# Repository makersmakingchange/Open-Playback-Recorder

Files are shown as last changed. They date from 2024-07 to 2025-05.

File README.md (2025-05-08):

# Open Playback Recorder

The Open Playback Recorder can record three lists of voice messages that its user can playback via the trigger of an accessible button connected through a 3.5 mm mono jack. It aims to assist users with communication difficulties by giving them alternative methods to engage in conversation. This device has functionality similar to AbleNet’s Big Mack or Step by Step.  

The device is comprised of off-the-shelf electronics and 3D printed parts. The overall cost of materials is about $90 (plus $8 for component shipping).

The Open Playback Recorder is Open Assistive Technology (OpenAT) and is certified as Open Source Hardware by the Open Source Hardware Association under the OSHWA UID [CA000050](https://certification.oshwa.org/ca000050.html). Under the terms of the open source licenses, the device may be built, used, and improved upon by anyone.

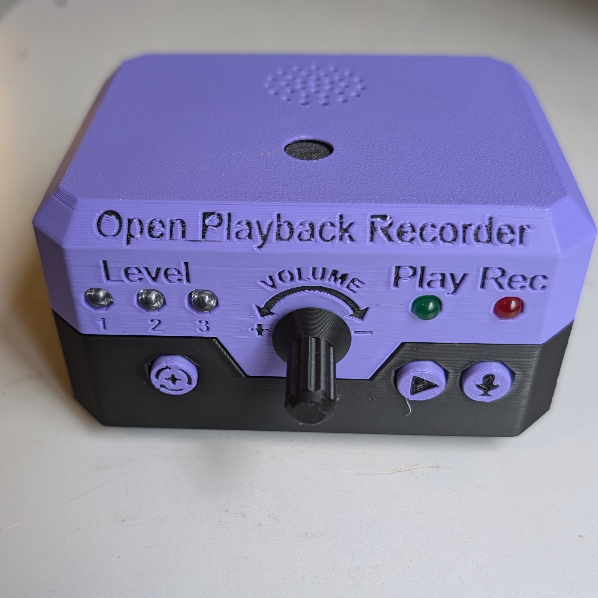
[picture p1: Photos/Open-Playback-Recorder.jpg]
An Open Playback Recorder with two Interact Switches with custom toppers.


## Makers Making Change Assistive Device Library
 - https://www.makersmakingchange.com/s/product/open-playback-recorder/01tJR000003DNOVYA4

## How to Obtain the Device
### 1. Do-it-Yourself (DIY) or Do-it-Together (DIT)

This is an open-source assistive technology, so anyone is free to build it. All of the files and instructions required to build the device are contained within this repository. Refer to the Maker Guide below.

### 2. Request a build of this device

You may also submit a build request through the [MMC Library Page](https://www.makersmakingchange.com/s/product/open-playback-recorder/01tJR000003DNOVYA4) to have a volunteer maker build the device. As the requestor, you are responsible for reimbursing the maker for the cost of materials and any shipping.

### 3. Build this device for someone else

If you have the skills and equipment to build this device, and would like to donate your time to create the device for someone who needs it, visit the [MMC Maker Wanted](https://makersmakingchange.com/maker-wanted/) section.

## Build Instructions

### 1. Read through the Maker Guide
The [Maker Guide](/Documentation/Open_Playback_Recorder_Maker_Guide.pdf)  contains all the necessary information to build this device, including tool lists, assembly instructions, programming instructions (if applicable) and testing.

### 2. Order the Off-The-Shelf Components
The [Bill of Materials](/Documentation/Open_Playback_Recorder_BOM.xlsx) lists all of the parts and components required to build the Open Playback Recorder. Several  components for this device will need to be ordered online.

### 3. Order the PCBs
The [PCB files](/Build_Files/PCB_Files) contain the Gerber files needed to order the PCBs, and instructions for how to order PCBs can be found in the [Maker Guide](/Documentation/Open_Playback_Recorder_Maker_Guide.pdf)

### 4. Print the 3D Printable components
All of the files and individual print files can be in the [/Build_Files/3D_Printing_Files](/Build_Files/3D_Printing_Files/) folder.

### 5. Assemble the Open Playback Recorder
Reference the [Maker Guide](/Documentation/Open_Playback_Recorder_Maker_Guide.pdf) for the tools and steps required to build each portion.

## How to improve this Device
As open source assistive technology, you are welcomed and encouraged to improve upon the design. 

## Files
### Documentation
| Document             | Version | Link |
|----------------------|---------|------|
| Design Rationale     | 2.0     | [Open_Playback_Recorder_Design_Rationale](/Documentation/Open_Playback_Recorder_Design_Rationale.pdf)     |
| Maker Guide          | 2.0     | [Open_Playback_Recorder_Maker_Checklist](/Documentation/Open_Playback_Recorder_Maker_Guide.pdf)     |
| Bill of Materials    | 2.0     | [Open_Playback_Recorder_Bill_of_Materials](/Documentation/Open_Playback_Recorder_BOM.xlsx)     |
| User Guide           | 2.0     | [Open_Playback_Recorder_User_Guide](/Documentation/Open_Playback_Recorder_User_Guide.pdf)    |
| Changelog            | 2.0     | [Open_Playback_Recorder_Changelog](CHANGES.txt)     |

### Design Files
 - [CAD Files](/Design_Files/CAD_Design_Files)
 - [PCB Files](/Design_Files/PCB_Files)

### Build Files
 - [3D Printing Files](/Build_Files/3D_Printing_Files)
 - [PCB Files](/Build_Files/PCB_Files)

### Software Files
 - [Software Files](/Build_Files/Firmware_Files)

## Attribution
Designers:
 - Neil Squire Society / Makers Making Change

Contributors:
 - Brad Wellington
 - Erik Steinthorson
 - Jake McIvor
 - Derrick Andrews

## License
Copyright (c) 2024 Neil Squire / Makers Making Change.

This repository describes Open Hardware:
 - Everything needed or used to design, make, test, or prepare the Open Playback Recorder is licensed under the [CERN 2.0 Weakly Reciprocal license (CERN-OHL-W v2) or later](https://cern.ch/cern-ohl ) .
 - All software is under the [GNU General Public License v3.0 (GPL-3.0)](https://www.gnu.org/licenses/gpl.html).
 - Accompanying material such as instruction manuals, videos, and other copyrightable works that are useful but not necessary to design, make, test, or prepare the Open Playback Recorder are published under a [Creative Commons Attribution-ShareAlike 4.0 license (CC BY-SA 4.0)](https://creativecommons.org/licenses/by-sa/4.0/) .

You may redistribute and modify this documentation and make products using it under the terms of the [CERN-OHL-W v2](https://cern.ch/cern-ohl).
This documentation is distributed WITHOUT ANY EXPRESS OR IMPLIED WARRANTY, INCLUDING OF MERCHANTABILITY, SATISFACTORY QUALITY AND FITNESS FOR A PARTICULAR PURPOSE.
Please see the CERN-OHL-W v2 for applicable conditions.

Source Location: https://github.com/makersmakingchange/Open-Playback-Recorder

---

<!-- ABOUT MMC START -->
## About Makers Making Change
[Makers Making Change Logo](https://www.makersmakingchange.com/)

Makers Making Change is a program of [Neil Squire](https://www.neilsquire.ca/), a Canadian non-profit that uses technology, knowledge, and passion to empower people with disabilities.

Makers Making Change leverages the capacity of community based Makers, Disability Professionals and Volunteers to develop and deliver affordable Open Source Assistive Technologies.

 - Website: [www.MakersMakingChange.com](https://www.makersmakingchange.com/)
 - GitHub: [makersmakingchange](https://github.com/makersmakingchange)
 - Twitter: [@makermakechange](https://twitter.com/makermakechange)
 - Instagram: [@makersmakingchange](https://www.instagram.com/makersmakingchange)
 - Facebook: [makersmakechange](https://www.facebook.com/makersmakechange)
 - LinkedIn: [Neil Squire Society](https://www.linkedin.com/company/neil-squire-society/)
 - Thingiverse: [makersmakingchange](https://www.thingiverse.com/makersmakingchange/about)
 - Printables: [MakersMakingChange](https://www.printables.com/@MakersMakingChange)

### Contact Us
For technical questions, to get involved, or to share your experience we encourage you to [visit our website](https://www.makersmakingchange.com/) or [contact us](https://www.makersmakingchange.com/s/contact).
<!-- ABOUT MMC END -->

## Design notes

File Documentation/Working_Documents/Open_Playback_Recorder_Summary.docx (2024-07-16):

# Product Information

## Product Name

Open Playback Recorder

## Device Category

Adapted Toys

Aids for Daily Living (ADL)

Assistive Switches

Communication Aids (AAC)

Computer Access

Environmental Controls

Gaming

Keyguard

Kits

LipSyncs

Mounting

Recreation and Leisure

Seating and Positioning

Switch Interfaces

Writing Aids

## User Value Statement

The Open Playback Recorder is an open-source device that can record three lists of voice messages that its user can playback via the trigger of an accessible button connected through a 3.5 mm mono jack. It aims to assist users with communication difficulties by giving them alternative methods to engage in conversation. This device has functionality similar to AbleNet’s Big Mack or Step by Step.

## Designer

Design by Neil Squire Society/Makers Making Change

# Device Info

## Overview

This device can record and store three separate lists of messages, which can then be sequentially played back using a 3.5mm jack or an onboard button. It is designed for users with difficulty communicating, and can allow them to choose from a list of messages for three separate situations.

## Disability Type

Select one or more disability types:

Agility / Dexterity

Arthritis

Cognitive

Hearing

Mobility

Mobility

Other

Pain

SCI

Vision

## Disability Type Description

This device is designed for users that have difficulty with communication and need a communication aid. This device can store three different sets of messages for use in three different situations.

## How To Use

### Setup

Connect two assistive switches, one to the jack labeled PLAY, and one to the jack labeled LEVEL.

### Power On

To power on the device, toggle the switch on the side of the device from OFF to ON.

### Message Recording

To record one or more messages, the device needs to be in Record Mode. The device will record messages to the currently selected level.

Step 1. To engage “Record Mode” hold down the REC button for 2 seconds. When Record Mode is engaged, the REC LED will turn red and remain solid.

Note: When Record Mode is engaged, all previous messages on that level will be erased.

Step 2. To start message recording, press and hold the PLAY button or assistive switch connected to the play jack. The REC LED will flash red. Record the message into the microphone and release the button to end and save the message. The RED LED will once again turn red and remain solid.

Step 3. To record additional messages, repeat Step 2.

Note: These messages will later by played back in the same order they were recorded.

Step 4. When the desired messages have been recorded, press the REC button to exit Record Mode. The red REC LED will turn off.

### Message Playback

To play back a message, press an assistive switch connected to the play jack. This will play a message from the current recording level. The play button on the device itself will also allow a secondary user to play a message. Continuing to press the button will cycle through all the messages on that level.

To change the message level, press an assistive switch connected to the level jack. The level shift button on the device will also allow a secondary user to change the message level. The current level will be indicated by the three blue LEDs on the left side of the device.

## Estimated Cost

The estimated material cost of the device:

$0 - $10

$11 - $25

$26 - $50

$51 - $100

$101 - $250

$250+

## Attribution

Design by Neil Squire Society/Makers Making Change

# Maker Info

## Project Skills

3D Printing

Custom PCB

Electronics

Laser Cutting

Mechanics

Other

Software

Soldering

Woodworking

## Skills Description

The primary skill used in this build is soldering. The circuit is constructed on a PCB, with all the components soldered to it.

## Tools Needed

3D Printer

Common Hand Tools

Common Power Tools

Laser Cutter

Soldering Iron

Specialized Tooling

## Print time (hrs)

3.5 hrs

## Assembly time (hrs)

0.5 hrs

## Build Instructions

The main work on this build involves soldering together two circuits on PCBs, one for each half of the enclosure.

## Download Link

## https://github.com/makersmakingchange/Open-Playback-Recorder/archive/refs/heads/main.zip

## Project Link

## https://github.com/makersmakingchange/Open-Playback-Recorder

# License

## License

- Everything needed or used to design, make, test, or prepare the Open Playback Recorder is licensed under the CERN 2.0 Weakly Reciprocal license (CERN-OHL-W v2) (https://cern.ch/cern-ohl) or later .

- All software is under the GNU General Public License v3.0 (GPL-3.0) (https://www.gnu.org/licenses/gpl.html).

- Accompanying material such as instruction manuals, videos, and other copyrightable works that are useful but not necessary to design, make, test, or prepare the Open Playback Recorder are published under a Creative Commons Attribution-ShareAlike 4.0 license (CC BY-SA 4.0) (https://creativecommons.org/licenses/by-sa/4.0/).

© 2024 by Neil Squire Society This work is licensed under the CC BY SA 4.0 License: http://creativecommons.org/licenses/by-sa/4.0 Page 1 of 2

V2.0 | June 2024 Open Playback Recorder Summary

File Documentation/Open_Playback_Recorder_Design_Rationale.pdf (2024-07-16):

V2.0 | June 2024

## Open Playback Recorder

## DESIGN RATIONALE

© 2022-2024 by Neil Squire / Makers Making Change This work is licensed under the CC BY SA 4.0 License: http://creativecommons.org/licenses/by-sa/4.0
Files available at https://github.com/makersmakingchange/Open-Playback-Recorder/ | Page 1 of 44

### Introduction

The Open Playback Recorder is an open-source device that can record three lists of voice messages that its user can playback via the trigger of an accessible button connected through a 3.5 mm mono jack. It aims to assist users with communication difficulties by giving them alternative methods to engage in conversation. This device has functionality similar to AbleNet’s Big Mack or Step by Step.

### Research

### Commercial Products

Big Mack
The Big Mack is an audio recording and playback device that costs between $150 and $200. It can record a message with a maximum length of two minutes via the trigger of a record button. The stored message can then be played back after the trigger of a large accessible button. It has adjustable volume and is battery powered by a 9V battery.

Message from AbleNet (ablenetinc.com) (https://www.ablenetinc.com/bigmack/)

Message storage procedure (From AbleNet):

1. Ensure you've properly installed a 9V Alkaline battery into your device
2. Turn the device on
3. Press and hold the Record Switch until the LED lights up solid Red, then release the switch
4. Press and hold down the main switch top of your device. You will see the LED flashes Red when recording.
5. Speak your message into the communication device, then release the switch top to complete the recording
6. When finished, press the Record Switch one time to exit record mode

Button size: ~12 cm diameter

Little Mack: Little Mack = ~6 cm

Big Step by Step
Costing between around $220, the Big Step by Step is a similar product to the Big Mack with two additional features. This device can record a sequential list of messages with a maximum total length of four minutes. Each message in the list is played one by one for each press of the playback button. The second feature included is a 3-level switch where each level stores a unique list of messages.

## DESIGN RATIONALE

Files available at https://github.com/makersmakingchange/Open-Playback-Recorder/ | Page 2 of 44

BIG Step-by-Step (ablenetinc.com) (https://www.ablenetinc.com/big-step-by-step/)

Message Recording Procedure (From AbleNet)

1. Add one alkaline 9-volt battery to device (battery not included).
2. Turn device on.
3. Select desired level.
4. Press and hold record button until recording indicator light turns on.
5. Press and hold colored switch top. Begin speaking into microphone after you hear beep.
6. When done recording message, release colored switch top.
7. Repeat steps 5 and 6 to record additional messages.
8. Press the record button to turn the recording indicator light off.
9. Optional: Select a different recording level to record a second and third set of messages.
10. Adjust volume as needed.
11. Your device is ready to use.

Little Mack Options
Both styles of the Big Mack are also offered in smaller sizes for a similar cost.

https://www.spectronics.com.au/product/littlemack-communicator-enhanced

https://www.spectronics.com.au/product/little-step-by-step-communicator-with-levels-enhanced

Pet Training Button
There are a series of audio playback buttons designed for the use of trained pets. They are inexpensive, costing between $10 to $40 with the drawback of back functionality. They can record and store a single message with a maximum length of 10 to 30 seconds. Stored messages are played back via the trigger of a small button and has no volume control.

Neutral Record Talking Button : Amazon.ca: Office Products (https://www.amazon.ca/Neutral-Record-Talking-Button/dp/B073S3BKN6)

### DIY Projects

Project | Demonstrates | Link
Arduino Spy Bug | • Using Micro SD Modules with Arduino • Using microphone • Saving WAV files onto a micro-SD card | Make Your Own Spy Bug (Arduino Voice Recorder) : 5 Steps (with Pictures) -Instructables (https://www.instructables.com/Make-Your-Own-Spy-Bug-Arduino-Voice-Recorder/)
Arduino Spy Bug Remix | • Similar Project • Different micro controller | Simple Arduino Voice Recorder for Spy Bug Voice Recording (circuitdigest.com) (https://circuitdigest.com/microcontroller-projects/simple-arduino-voice-recorder-for-spy-bug-voice-recording)
Arduino Audio Player | • Audio Amp • Playing WAV files | Audio Player Using Arduino With Micro SD Card : 7 Steps (with Pictures) - Instructables (https://www.instructables.com/Audio-Player-Using-Arduino-With-Micro-SD-Card/)

## DESIGN RATIONALE

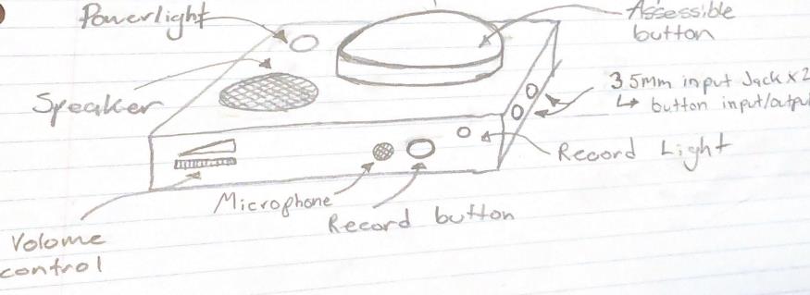
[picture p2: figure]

Files available at https://github.com/makersmakingchange/Open-Playback-Recorder/ | Page 3 of 44
Arduino Mp3 Player | • Similar project to Arduino Audio Player | Arduino Mp3 Player : 5 Steps -Instructables (https://www.instructables.com/Arduino-Mp3-Player/)
SD Card Experiments | • Using SD card modules with Arduino • Applications of SD cards | SD Card Experiments with Arduino | DroneBot Workshop (https://dronebotworkshop.com/sd-card-arduino/)

### Requirements

### Goals

G01 | Record and store a message with a minimum allowable record time of 4 minutes
G02 | Play stored message after trigger of an accessible button
G03 | Adjustable playback volume with maximum level loud enough to be heard within a room

### Functional Requirements

F01 | Total print time under 24 hours
F02 | Battery powered with easily obtainable batteries
F03 | Ability to be trigger by an external switch via a 3.5 mm mono cable

### Non-functional Requirement

NF01 | Exchangeable button cap designs for different needs of the user.
NF02 | Capable of interconnecting additional Open Playback Buttons
NF03 | Easy access to batteries for exchanging them.
NF04 | Must be easily cleaned

### Constraints

C01 Capable of being constructed using basic maker tools.

### Ideation

Idea #1: Basic concept with necessary components.

## DESIGN RATIONALE

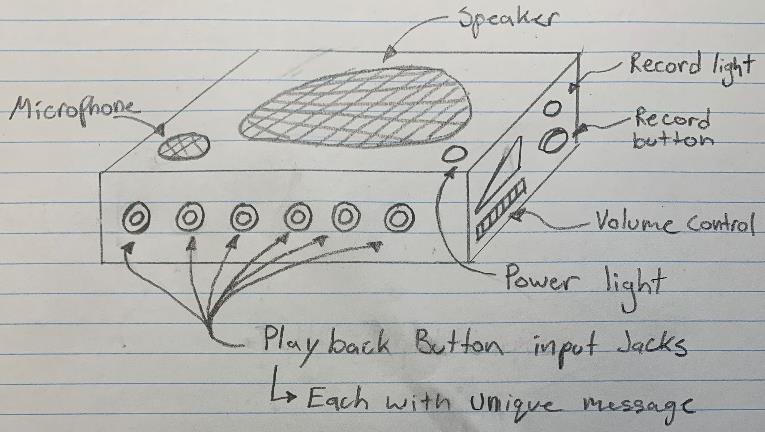
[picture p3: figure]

Files available at https://github.com/makersmakingchange/Open-Playback-Recorder/ | Page 4 of 44

Idea #2: Modular design utilizing external switches.

Instead of fitting all the electronics inside a large button, another idea could be to have a single unit to handle message recording and playback. An array of external buttons could then be plugged into one or many of the 3.5 mm input jacks. Each button would control its own message or sequential list of messages. This would allow for more space to fit larger speakers and electronics. The large assessable button would become its own device to be designed.

### Conceptual Design

### Options for Audio Recording and Playback

Option 1: Use of Voice Record and Playback Module
System | Possible Product | Notes: | Cost
Voice Record and Playback | SEN0197 DFRobot | Development Boards, Kits, Programmers | DigiKey (https://www.digikey.ca/en/products/detail/dfrobot/SEN0197/6588582) | SEN0197 • 10s Record time • Connects easily with Arduino | ~$10
| NC-ISD1620B Nuvoton Technology Corporation | Development Boards, Kits, Programmers | DigiKey (https://www.digikey.ca/en/products/detail/nuvoton-technology-corporation/NC-ISD1620B/1228829) | NC-ISD1620B • Single message • 6.6s to 40s record time | ~$10
| 107020007 Seeed Technology Co., Ltd | Development Boards, Kits, Programmers | DigiKey (https://www.digikey.ca/en/products/detail/seeed-technology-co-ltd/107020007/12177149) | Grove – Recorder V2.) • Volume control • 8Ω/2W Speaker • 8s to 20s record time | ~$10
Overall Notes | These modules are simple and easy to use while remaining inexpensive but may be to limiting functionally. As part of the requirements for this project, 4 minutes of record time is needed but these modules are intended for much shorter recordings. | | Total ~$30

## DESIGN RATIONALE

Files available at https://github.com/makersmakingchange/Open-Playback-Recorder/ | Page 5 of 44

Option 2: Use of Micro SD Storage
System | Component | Possible Product | Notes: | Cost
Controller | Arduino Micro | A000053 Arduino | Development Boards, Kits, Programmers | DigiKey (https://www.digikey.ca/en/products/detail/arduino/A000053/4486332) | Cheaper options? | ~$25
Audio Playback | Audio Amplifier Module | 2130 Adafruit | Mouser Canada (https://www.mouser.ca/ProductDetail/485-2130) | Pam8302A: • Mono sound • Shut off capabilities | ~$6
| Speaker | 3351 Adafruit | Mouser Canada (https://www.mouser.ca/ProductDetail/485-3351) | 3W 4 Ohm, 2.8” x 1.2” • Easy to mount • Recommended for Pam8302A or MAX98357A | ~$6
| Potentiometer: Volume Control | 3395 Adafruit | Mouser Canada (https://www.mouser.ca/ProductDetail/485-3395) | • 10K • Includes switch for on/off • Clicks in off position | ~$2
Audio Recording/ Storage | Micro Sd Reader: | 254 Adafruit | Mouser Canada (https://www.mouser.ca/ProductDetail/485-254) | Built in 3v-5v regulator | ~$10
| Micro Sd Card: Message Storage | COM-15107 SparkFun | Mouser Canada (https://www.mouser.ca/ProductDetail/474-COM-15107) | 1GB but many size options | ~$10
| Mic with Amp | 1713 Adafruit | Mouser Canada (https://www.mouser.ca/ProductDetail/485-1713) | | ~$10
Overall Notes | There is an added cost and complexity to using an SD card for storage. This solution requires an SD card module, SD card, audio recording module and must use a micro controller. However, this concept allows the full control of functionality. It will be possible to add modes for multiple message capabilities, i.e.: Big Mack mode, step by step mode, voice repeat mode, etc. Almost no limit on record time. | | | Total ~70

### Playing Audio Files

Recording and Playing Audio with Wav Files

For the Arduino use wav files for audio recording and playback, the TMRpcm library must be downloaded and used. This library is capable of reading wav files off an SD card and outputting the audio signal through a selected port on the Arduino. It must be noted that by default, the audio recording capabilities are disabled. To enable these features, the library configurations must be edited.

In the file pcmConfig.h file, there are two sections that must be edited:

In the General User Defines section, the “//#define buffSize 128” line of code must be uncommented by removing the “//” from in front.

In the Advanced User Defines section, at the bottom, lines “//#define ENABLE_RECORDING” and “//#define BLOCK_COUNT 10000UL” must also be uncommented.

## DESIGN RATIONALE

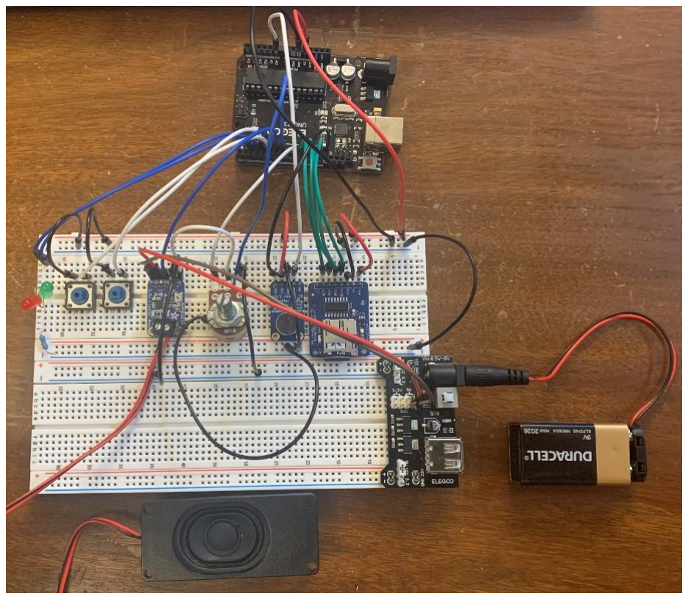
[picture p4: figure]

Files available at https://github.com/makersmakingchange/Open-Playback-Recorder/ | Page 6 of 44

### Using Audacity to Add Sound Indicators

Audacity is a program that can be used to create audio files. If these files are going to be played from the Arduino using the TMRpcm library, the files must be created and saved correctly.

Step 1.
At the bottom right corner, select Project Rate (Hz), and set to 3200, 22050, 16000, or 11025

Note: 16000 Hz is the default sample rate for the TMRpcm library.

Step 2.
At the top of the screen, click Tracks -> Add New -> and select Mono Track. Create one or more of the mono tracks to create the sound file
Step 3.
Once the sound is complete, click File -> Export -> Export Audio… -> save as type: Other uncompressed files, Header: WAV, Encoding: Signed 8-bit PCM

The audio file can now be saved and added to the device Micro SD card to be used by the TMRpcm library.

### V0.1 Proof-of-Concept Prototype

## DESIGN RATIONALE

Files available at https://github.com/makersmakingchange/Open-Playback-Recorder/ | Page 7 of 44

### POC Components

System | Component | Possible Product | Notes:
Controller | Micro Controller | Arduino Uno | Cheaper options?
Audio Playback | Audio Amplifier Module | 2130 Adafruit | Mouser Canada (https://www.mouser.ca/ProductDetail/485-2130) | Pam8302A: • Mono sound • Shut off capabilities
| Speaker | 3351 Adafruit | Mouser Canada (https://www.mouser.ca/ProductDetail/485-3351) | 3W 4 Ohm, 2.8” x 1.2” • Easy to mount. • Recommended for Pam8302A or MAX98357A
| Capacitor | | Protect speaker amplifier input voltage. • For use with PAM8302A 0.1uF to 0.22uF is ideal • low leakage tantalum or ceramic capacitor is the best choice
| Potentiometer: Volume Control | 3395 Adafruit | Mouser Canada (https://www.mouser.ca/ProductDetail/485-3395) | • 10K Ohm • Includes switch for on/off. • Clicks in off position
Audio Recording/ Storage | Micro SD Reader: | 254 Adafruit | Mouser Canada (https://www.mouser.ca/ProductDetail/485-254) | • Built in 3v-5v regulator. • Connects to SPI pins
| Micro SD Card: Message Storage | COM-15107 SparkFun | Mouser Canada (https://www.mouser.ca/ProductDetail/474-COM-15107) | 1GB but many size options
| Mic with Amp | 1713 Adafruit | Mouser Canada (https://www.mouser.ca/ProductDetail/485-1713)
Basic Control | Playback Button | B3F-5050 Omron Electronics | Mouser Canada (https://www.mouser.ca/ProductDetail/Omron-Electronics/B3F-5050?qs=dOLq8QE0Pqqk%2FO9x2OpTQw%3D%3D) | Simple press button
Record Button
Power/Play Light | LTL2R3KGD-EM Lite-On | Mouser Canada (https://www.mouser.ca/ProductDetail/Lite-On/LTL2R3KGD-EM?qs=xb8aMrBSZRJFqGZErUW7HQ%3D%3D) | Simple red and green LED’s
Record Light | LTL2R3KRD-EM Lite-On | Mouser Canada (https://www.mouser.ca/ProductDetail/Lite-On/LTL2R3KRD-EM?qs=xb8aMrBSZRL5MG5wqCOHaQ%3D%3D)

## DESIGN RATIONALE

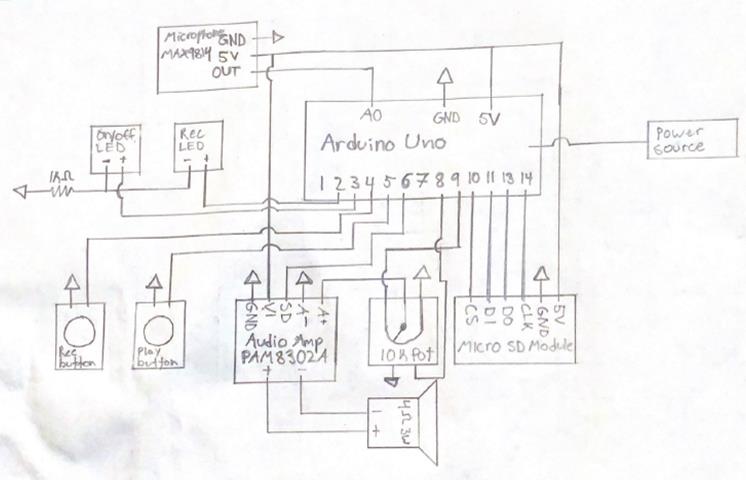
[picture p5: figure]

Files available at https://github.com/makersmakingchange/Open-Playback-Recorder/ | Page 8 of 44

### POC Wiring Diagram

### POC Device Functionality

Controls: | Playback Button: play button for primary user
| Record Button: small button for secondary user
| Volume Knob: small dial for secondary user
Indicators: | Power/Playback light: Green LED
| Record light: Red LED

Functionality: Power On/Off: small dial for secondary user.

| • Turn volume knob past minimum to power on device. • Power light turns on. • Turning the dial controls the volume output. • Clicking the dial into the minimum position turns the device off. • All lights turn off.
| Record Mode: Accessed via record button.
| • Hold Record Button for 2 seconds to engage record mode • Messages in storage are deleted. • Record light turns on.

## DESIGN RATIONALE

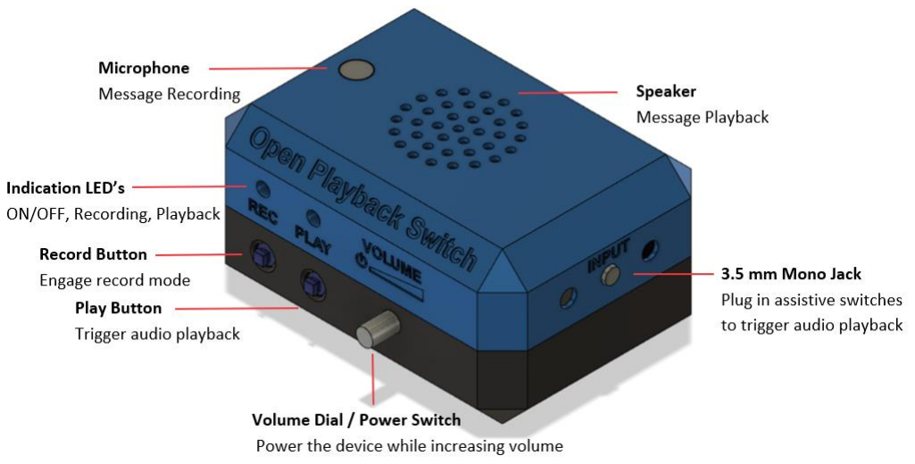
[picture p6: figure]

Files available at https://github.com/makersmakingchange/Open-Playback-Recorder/ | Page 9 of 44
- Press and hold Playback Button to record a message.
- Record light flashes during recording.

Message Playback: Accessed via play button.

- Press playback button to play message.
- Each trigger plays next message in queue.
- Goes back to first message after last message in queue is played.

### V0.2 MVP Design

### MVP Components

Component | Cost | Link
Micro Controller (Arduino Micro) | $30.50 | A000093 Arduino | Mouser Canada (https://www.mouser.ca/ProductDetail/782-A000093)
Audio Amplifier (Pam8302) | $5.45 | 2130 Adafruit | Mouser Canada (https://www.mouser.ca/ProductDetail/485-2130)
Mono Speaker (4Ω 3W ) | $5.45 | 3351 Adafruit | Mouser Canada (https://www.mouser.ca/ProductDetail/485-3351)
Potentiometer with Switch (Log) | $2.07 | 3481 Adafruit | Mouser Canada (https://www.mouser.ca/ProductDetail/485-3481)
Micro SD Reader | $10.35 | 254 Adafruit | Mouser Canada (https://www.mouser.ca/ProductDetail/485-254)
Micro SD Card | $9.49 | COM-15107 SparkFun | Mouser Canada (https://www.mouser.ca/ProductDetail/474-COM-15107)
Microphone (MAX9814) | $10.97 | 1713 Adafruit | Mouser Canada (https://www.mouser.ca/ProductDetail/485-1713)

## DESIGN RATIONALE

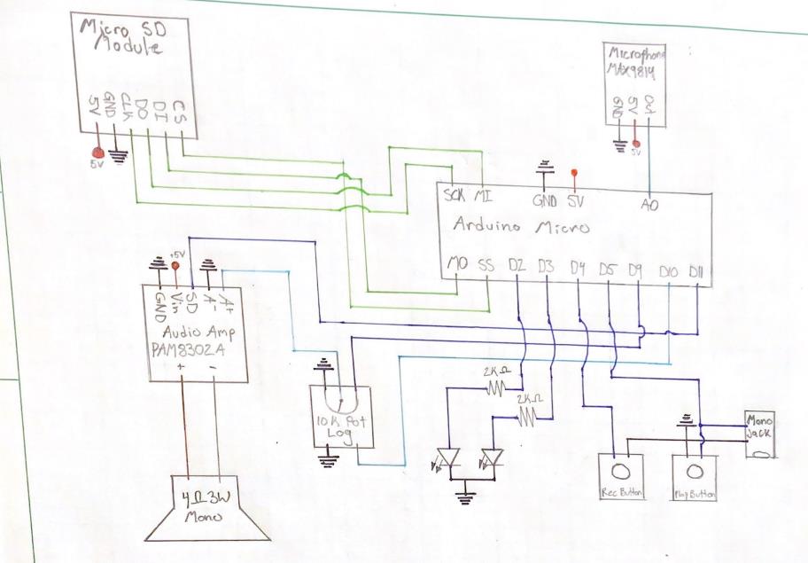
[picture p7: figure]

Files available at https://github.com/makersmakingchange/Open-Playback-Recorder/ | Page 10 of 44
Buttons (B3F-5050) | $1.52 | B3F-5050 Omron Electronics | Mouser Canada (https://www.mouser.ca/ProductDetail/Omron-Electronics/B3F-5050?qs=dOLq8QE0Pqqk%2FO9x2OpTQw%3D%3D)
3.5 mm Mono Jack | $1.95 | 35RAPC2AV Switchcraft | Mouser Canada (https://www.mouser.ca/ProductDetail/Switchcraft/35RAPC2AV?qs=I3kMT7EEIOWP5G1fR6CxcA%3D%3D)
Green LED (5 mm) | $0.44 | LTL2R3KGD-EM Lite-On | Mouser Canada (https://www.mouser.ca/ProductDetail/Lite-On/LTL2R3KGD-EM?qs=xb8aMrBSZRJFqGZErUW7HQ%3D%3D)
Red LED (5 mm) | $0.44 | LTL2R3KRD-EM Lite-On | Mouser Canada (https://www.mouser.ca/ProductDetail/Lite-On/LTL2R3KRD-EM?qs=xb8aMrBSZRL5MG5wqCOHaQ%3D%3D)
Resistor (1k Ω) | $0.66 | MBA02040C1001FRP00 Vishay / Beyschlag | Mouser Canada (https://www.mouser.ca/ProductDetail/Vishay-Beyschlag/MBA02040C1001FRP00?qs=LkqrmUh5PILp63ntvCnX0w%3D%3D)
Proto Half Breadboard | $6.21 | 1609 Adafruit | Mouser Canada (https://www.mouser.ca/ProductDetail/485-1609)
Male Through Hole Header | $0.80 | https://www.mouser.ca/ProductDetail/910-HDR100IMP40MGVTH (https://www.mouser.ca/ProductDetail/910-HDR100IMP40MGVTH)
Female Through Hole Header | $3.80 | HDR100IMP40F-G-V-TH Chip Quik | Mouser Canada (https://www.mouser.ca/ProductDetail/Chip-Quik/HDR100IMP40F-G-V-TH?qs=Wj%2FVkw3K%252BMB%252BpQKGESbrjQ%3D%3D)
Notes: | The MVP device uses many of the same electrical components as the POV. The key differences are: • A logarithmic potentiometer is used for increased volume control. • An Arduino Micro is used to decrease the size. • A mono jack is wired in parallel to the Play Button. • Electrical components are soldered to a protoboard. • Powered by a 9V battery in series with the power switch.

### MVP Wiring Diagram

### Feature Set

- Modular (i.e., standalone)

## DESIGN RATIONALE

Files available at https://github.com/makersmakingchange/Open-Playback-Recorder/ | Page 11 of 44

The MVP will be a modular device intended to be used with external switches connected to a 3.5 mm mono jack

User Controls
- Input Jack
- Playback / Test Button
- Recording Button
- Volume Knob
- Integrated power control

Indicators
- PLAY LED
- Green LED
- Turns on while device is on
- Flashes during message playback
- REC LED
- Red LED
- Turns on while in record mode
- Flashes during message recording

Operating the device

Power On/Off
- Turn volume knob fully counterclockwise until it clicks to turn off device
- Turn

Record Mode
- Hold Record Button for 2 seconds to engage record mode
- Messages in storage are deleted
- Record light turns on
- Press and hold Playback Button to record a message
- Record light flashes during recording

Message Playback
- Press playback button to play message
- Each trigger plays next message in queue
- Goes back to first message after last message in queue is played.

### Testing

Recording is great; tricky to replace batteries

One box, multiple switches

## DESIGN RATIONALE

Files available at https://github.com/makersmakingchange/Open-Playback-Recorder/ | Page 12 of 44

Grandview testing

“The recorder is great! It was a bit tricky changing the battery because of all the wires and the challenge of not being able to open it all the way, but the sound quality and volume adjustment and general use are really easy!

It would be really neat to have one box where you could plug in two switches for different messages but that would probably be way more complicated.

“It's such a great device!!!!”

### Opportunities for Improvement

1. Battery cover for easy replacement.
2. Separate power/volume control switches.
3. Volume knob for volume potentiometer.
4. Multiple input jacks.
5. ¼”-20 mount

### V0.3 Design

### Component Considerations

To reduce cost, complexity, and meet some of the opportunities for improvement from the MVP, the following components will be investigated to determine if there are more suitable options:

- Micro Controller
- Microphone
- SD Card Reader
- SD Card
- Audio Amplifier
- Speaker
- LED Indicators
- Volume Potentiometer
- 3-way switch
- On/off switch

## DESIGN RATIONALE

Files available at https://github.com/makersmakingchange/Open-Playback-Recorder/ | Page 13 of 44

Microcontroller Options
Possible Product | Cost | Power Output | Input Voltage | Notes:
Arduino Micro (Used with MVP) (https://www.mouser.ca/ProductDetail/Arduino/A000093?qs=B4lwOSfBLoKJean8vPGHVA%3D%3D) | ~$30 | 2.7 – 5.5V | 7 – 12V | Convenient choice while prototyping but not necessarily the best choice based on the price.
Adafruit Feather Adalogger (https://www.mouser.ca/ProductDetail/Adafruit/2795?qs=xE9dPqTLfL5QKg8UliiWEg%3D%3D) | ~30 | 3.3V Only | 5V USB or 4.2/3.7V Lipo | This board is being considered due to its integrated MicroSD reader. This saves the cost and complexity of wiring an external SD reader to the protoboard. However, this board can only output 3.3V which is not enough for the audio amplifier, which will result in an added cost to properly power it.
Arduino Nano (https://www.mouser.ca/ProductDetail/Arduino/ABX00033?qs=PzGy0jfpSMueXyfBfl2XSA%3D%3D) | ~$22.00 | 5V | 6 – 20V | Similar to the Micro. Will work for this project.
Seeeduino Nano (https://www.mouser.ca/ProductDetail/Seeed-Studio/102010268?qs=%252B6g0mu59x7KIlg%252BxI6sM2Q%3D%3D) | ~$10.50 | 5V | 6 – 20V | This inexpensive board has the identical pinouts to the Arduino Nano and should be compatible with all other components.
QT PY SAMD 21 (https://www.mouser.ca/ProductDetail/Adafruit/4600?qs=hd1VzrDQEGi752M4exorSA%3D%3D) | ~10.50 | 3.3 – 5V | 5V | There are a series of small microcontroller like this one from $5 - $15. This could help reduce the size of the device but does not have enough I/O pins.
Final Selection | As the Seeeduino Nano is the most similar and inexpensive microcontroller considered, it will be the board used for this final version.

Microphone Options
Possible Product | Cost | Input Voltage | Impedance | Notes:
MAX9814 (Used with MVP) (https://www.mouser.ca/ProductDetail/Adafruit/1713?qs=GURawfaeGuArxgrgUGiqIw%3D%3D) | ~$11.00 | 2.7 – 5.5V | | Includes amp. Automatic gain control
MAX4466 (https://www.mouser.ca/ProductDetail/Adafruit/1063?qs=GURawfaeGuDfuUUmMlF1tA%3D%3D) | ~$10.50 | 2.4 – 5V | | Includes amp. Fixed gain
Final Selection | Both microphones include an amplifier and gain control at a very similar price. We will proceed with the MAX9814 as it worked well with the MVP and performs well with noisy backgrounds.

Micro SD Card Reader Options
Possible Product | Cost | Power Input | Interface Type | Notes:
Adafruit 254 Micro SD Board (Used with MVP) (https://www.mouser.ca/ProductDetail/Adafruit/254?qs=GURawfaeGuAkwqCF4BmPzA%3D%3D) | ~$10.50 | 3.3V or 5V | SPI or SDIO
Adafruit 4682 Micro SD Board (https://www.mouser.ca/ProductDetail/Adafruit/4682?qs=hWgE7mdIu5TtvwzYJhYD8g%3D%3D) | ~$4.00 | 3.3V Only | SPI or SDIO | Won’t work with current micro controller directly
SparkFun DEV-13743 (https://www.mouser.ca/ProductDetail/SparkFun/DEV-13743?qs=WyAARYrbSna7AKzdOk0X8g%3D%3D) | ~$8.00 | 5V Only | SPI
SparkFun BOB-00544 (https://www.mouser.ca/ProductDetail/SparkFun/BOB-00544?qs=WyAARYrbSnZK7N50UQw0UQ%3D%3D) | ~6.50 | 3.3V Only | SPI | Won’t work with current micro controller directly
Final Selection: | Both boards that can operate using 5V are suitable for the final version. As the price difference between them is minimal, it will be best to proceed with the Adafruit 254 version.

## DESIGN RATIONALE

Files available at https://github.com/makersmakingchange/Open-Playback-Recorder/ | Page 14 of 44

Micro SD Card Options
Possible Product | Cost | Storage | Notes:
SparkFun COM-15107 (Used with MVP) (https://www.mouser.ca/ProductDetail/474-COM-15107) | ~$9.50 | 1GB | More storage than necessary
5249 Adafruit Micro SD (https://www.mouser.ca/ProductDetail/Adafruit/5249?qs=Rp5uXu7WBW%252B%2FlGiDAlYVUg%3D%3D) | ~$5.00 | 64Mb
5250 Adafruit Micro SD (https://www.digikey.ca/en/products/detail/adafruit-industries-llc/5250/15794636) | ~$5.50 | 128Mb | Not stocked by Mouser
5251 Adafruit Micro SD (https://www.digikey.ca/en/products/detail/adafruit-industries-llc/5251/15841479) | ~$6.00 | 256Mb | Not Stocked by Mouser
5252 Adafruit Micro SD (https://www.digikey.ca/en/products/detail/adafruit-industries-llc/5252/15841478) | ~$7.00 | 512Mb
Final Selection: | As message storage does not require much storage, the 64Mb option still fits within the scope if this project and is the most inexpensive option.

Audio Amplifier Options
Possible Product | Cost | Power | Impedance | Notes:
PAM8302 (Used with MVP) (https://www.mouser.ca/ProductDetail/Adafruit/2130?qs=GURawfaeGuAERP6YRZwNag%3D%3D) | ~$5.50 | 2.5W | 4Ohm
Final Selection | This amplifier works very well for the current setup as it can operate using the microcontroller power output. If the max volume needs to be increased further, the entire audio output system will need to be upgraded, along with an external power supply. To reduce cost and complexity, we will proceed with the PAM8402.

Speaker Options
Possible Product | Cost | Power | Impedance | Notes:
Adafruit Mono Enclosed (Used with MVP) (https://www.adafruit.com/product/3351) | ~$5.50 | 3W | 4Ohm | Enclosed mono speaker
Adafruit Mono Cone (https://www.adafruit.com/product/1314) | ~$3.00 | 3W | 4Ohm | 3” round speaker
Final Selection | Both speakers considered are ideal for the audio amplifier selected. We well proceed with the enclosed speaker as it offers more directional sound output.

LED Indicators
Possible Product | Cost | Colour | Size | Notes:
Dual LED’s (Used with MVP) (https://www.mouser.ca/ProductDetail/Lite-On/LTL2R3KGD-EM?qs=xb8aMrBSZRJFqGZErUW7HQ%3D%3D) | ~$1 ($0.5 per) | 1 red, 1 green | 5 mm | Two LED’s: One for playback/power indication, and the other for record mode/message recording indication.
Bi Colour LED | ~$1 | Red/green | 5 mm | Bi colour led that can turn green for message playback and red for recording.
Final Selection | To avoid confusion between the two LED’s and simplify the user interface, we will proceed with the Bi colour LED.

Volume Potentiometer
Possible Product | Cost | Resistance | Taper | Notes:
Adafruit Audio Pot (https://www.mouser.ca/ProductDetail/485-3481) | $2.07 | 10KOhm | Log | Includes on/off switch for power
BI Tech Pot (https://www.mouser.ca/ProductDetail/BI-Technologies-TT-Electronics/P160KNP-0QC20A10K?qs=56eeD6vBg8hi4UUaifEZ4Q%3D%3D) | $2.39 | 10KOhm | Audio
Final Selection | We will not include integrated power control in the volume dial, therefore a on/off switch is not required.

## DESIGN RATIONALE

Files available at https://github.com/makersmakingchange/Open-Playback-Recorder/ | Page 15 of 44

3-Position Switch
Possible Product | Cost | Switch Function | Type | Notes:
G-1328S-0000 CW Industries | Mouser Canada (https://www.mouser.ca/ProductDetail/CW-Industries/G-1328S-0000?qs=n1d6TrdN4SDIbOI8F4R%252B2A%3D%3D) | $3.16 | ON-ON-ON | Slide | Screw holes for easy mounting
S112032SS03Q C&K | Mouser Canada (https://www.mouser.ca/ProductDetail/CK/S112032SS03Q?qs=mfFuHy8STfJaTzKPmafJ7w%3D%3D) | $5.80 | ON-OFF-ON | Slide | Screw holes for easy mounting
G-329L-0019 CW Industries | Mouser Canada (https://www.mouser.ca/ProductDetail/CW-Industries/G-329L-0019?qs=n1d6TrdN4SBViBPpaPgSiw%3D%3D) | $2.44 | ON-ON-ON | Slide | Screw holes for easy mounting. Single pole, triple throw.
Final Selection | We will use the third option considered. More information can be found page 17 of the following recourse: Standard Switch Catalog S2120II03.doc (cwind.com) (https://www.cwind.com/pdf/Standard-Switch-Catalog-S2120-II-03-2.pdf)

On/Off Switch
Possible Product | Cost | Switch Function | Mount Style | Notes:
C1300ALAAA Bulgin | Mouser Canada (https://www.mouser.ca/ProductDetail/Bulgin/C1300ALAAA?qs=T3oQrply3y%252B3LOJGozZqzg%3D%3D) | $1.95 | ON-OFF | Snap In
RA11131123 E-Switch | Mouser Canada (https://www.mouser.ca/ProductDetail/E-Switch/RA11131123?qs=QtyuwXswaQhc6OwdGDJDiQ%3D%3D) | $0.93 | ON-OFF | Snap In | Has ON and OFF written on the side for easy use.
Final Selection | We will use the second option.

### Component Selection

System | Component | Selected Product | Quantity | Cost | Notes
Controller | Micro Controller | Seeeduino Nano (https://www.mouser.ca/ProductDetail/Seeed-Studio/102010268?qs=%252B6g0mu59x7KIlg%252BxI6sM2Q%3D%3D) | 1 | $10.49 | • Identical pinout to the Arduino Nano
Audio Playback | Audio Amplifier | PAM8302 (https://www.mouser.ca/ProductDetail/Adafruit/2130?qs=GURawfaeGuAERP6YRZwNag%3D%3D) | 1 | $5.45 | • 2.5W Class D
| Speaker | Adafruit Mono Enclosed (https://www.mouser.ca/ProductDetail/485-3351) | 1 | $5.45 | • 3W 4Ohm enclosed mono speaker
Message Storage | Micro SD Reader | Adafruit MicroSD Reader (https://www.mouser.ca/ProductDetail/485-254) | 1 | $10.35 | • 3V/5V regulator • SPI
| Micro SD Card | Adafruit MicroSD Card (https://www.mouser.ca/ProductDetail/Adafruit/5249?qs=Rp5uXu7WBW%252B%2FlGiDAlYVUg%3D%3D) | 1 | $4.83 | • 64Mb
Message Recording | Microphone/Amplifier | MAX9814 (https://www.mouser.ca/ProductDetail/485-1713) | 1 | $10.97 | • Integrated amplifier and automatic gain control
User Inputs | Volume Control | 10K Audio Pot (https://www.mouser.ca/ProductDetail/BI-Technologies-TT-Electronics/P160KNP-0QC20A10K?qs=56eeD6vBg8hi4UUaifEZ4Q%3D%3D) | 1 | $2.13 | • Log taper for audio control
| Play/Record Buttons | B3F-5050 | 2 | $1.52 ($0.76 per) | • Simple to solder and use • Easily mountable to enclosure
Buttons (https://www.mouser.ca/ProductDetail/Omron-Electronics/B3F-5050?qs=dOLq8QE0Pqqk%2FO9x2OpTQw%3D%3D)

## DESIGN RATIONALE

Files available at https://github.com/makersmakingchange/Open-Playback-Recorder/ | Page 16 of 44
| Switch Inputs | 3.5 mm Mono Jack (https://www.mouser.ca/ProductDetail/Switchcraft/35RAPC2AV?qs=I3kMT7EEIOWP5G1fR6CxcA%3D%3D) | 1 | $2.13 | • Standard for assistive switches • Threaded ring for easy mounting
| Power Control | On/Off Switch (https://www.mouser.ca/ProductDetail/E-Switch/RA11131123?qs=QtyuwXswaQhc6OwdGDJDiQ%3D%3D) | 1 | $0.93 | • Snap in rocker switch. • On/off labels
| Level Control | 3 Position Switch (https://www.mouser.ca/ProductDetail/CW-Industries/G-329L-0019?qs=n1d6TrdN4SBViBPpaPgSiw%3D%3D) | 1 | $2.44 | • 3 position slide switch with detents
Visual Indicators | Play/Record Light | Bi Colour RG LED (https://www.mouser.ca/ProductDetail/Kingbright/WP819SURKMGKW?qs=58z0TXQGVSRLNoI%2FJv9TJg%3D%3D) | 1 | $0.98 | • Red / Green LED
Power Supply | 9V Battery | Consumer 9V (https://www.mouser.ca/ProductDetail/Duracell/MN1604?qs=sGAEpiMZZMuXcNZ31nzYhRxIBnh8NwTszWVrE18PlWU%3D) | 1 | $3.48 | • Any standard 9V battery will work
| Battery Connector | 9V Battery Clip (https://www.mouser.ca/ProductDetail/563-HH-3449) | 1 | $1.79 | • Simple clip for connecting the battery
Assembly | Protoboard | Proto Half Breadboard (https://www.mouser.ca/ProductDetail/485-1609) | 1 | $6.21 | • Smallest size that can connect the micro controller, SD reader, and audio amp.
| Male Headers | Male Through Hole (https://www.mouser.ca/ProductDetail/910-HDR100IMP40MGVTH) | 2 | $1.60 ($0.80 per) | • Used for micro controller, audio amp and SD card reader
| Female Headers | Female Through Hole (https://www.mouser.ca/ProductDetail/Chip-Quik/HDR100IMP40F-G-V-TH?qs=Wj%2FVkw3K%252BMB%252BpQKGESbrjQ%3D%3D) | 2 | $3.80 ($1.90 per) | • Used for micro controller, audio amp and SD card reader.
| Resistors | 2K ohm Resistor (https://www.mouser.ca/ProductDetail/Vishay-Beyschlag/MBA02040C2001FCT00?qs=Q%252BviyuKCy%2FwudcV7dCRvqQ%3D%3D) | 2 | $0.66 ($0.33 per) | • Any standard 9V battery will work
| Screws | | | $
| | | | $
| | | | $

### Enclosure Design

The enclosure requires the following features:

- Input Jack (IMP)
- LED
- 2X Button (BUT)
- Volume Potentiometer (VOL)
- Microphone (MIC)
- Speaker Holes
- On/Off Switch (PS)
- 3 Position Level Select Switch (LS)

## DESIGN RATIONALE

Files available at https://github.com/makersmakingchange/Open-Playback-Recorder/ | Page 17 of 44

MVP LAYOUT

NOTES: Enclosure was made larger to incorporate a battery cover and only one input jack was used.

SOUND
MIC | HOLES

IMP

IMP

IMP

VOL

LED

LED

BUT BUT

## DESIGN RATIONALE

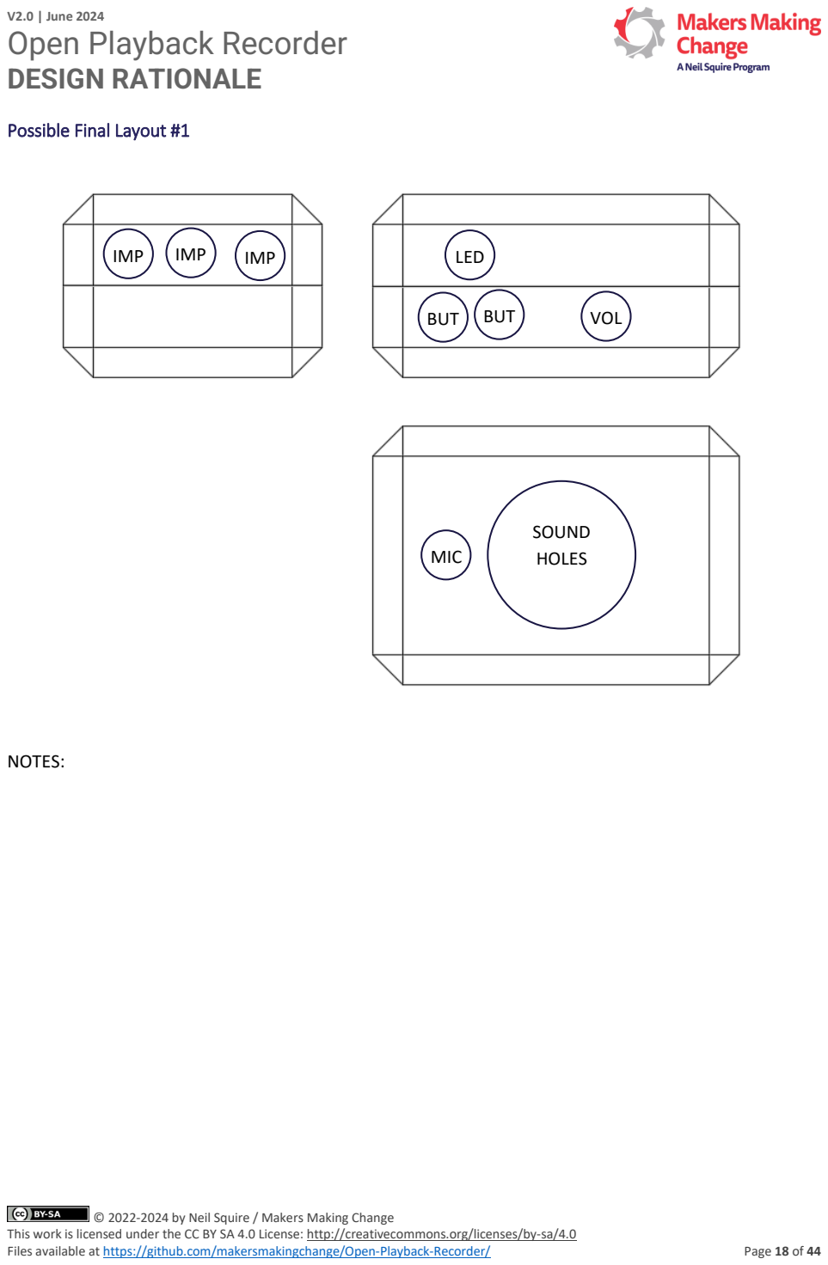
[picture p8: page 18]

Files available at https://github.com/makersmakingchange/Open-Playback-Recorder/ | Page 18 of 44

Possible Final Layout #1

NOTES:

SOUND
MIC | HOLES

IMP

IMP

IMP

VOL

LED

BUT BUT

## DESIGN RATIONALE

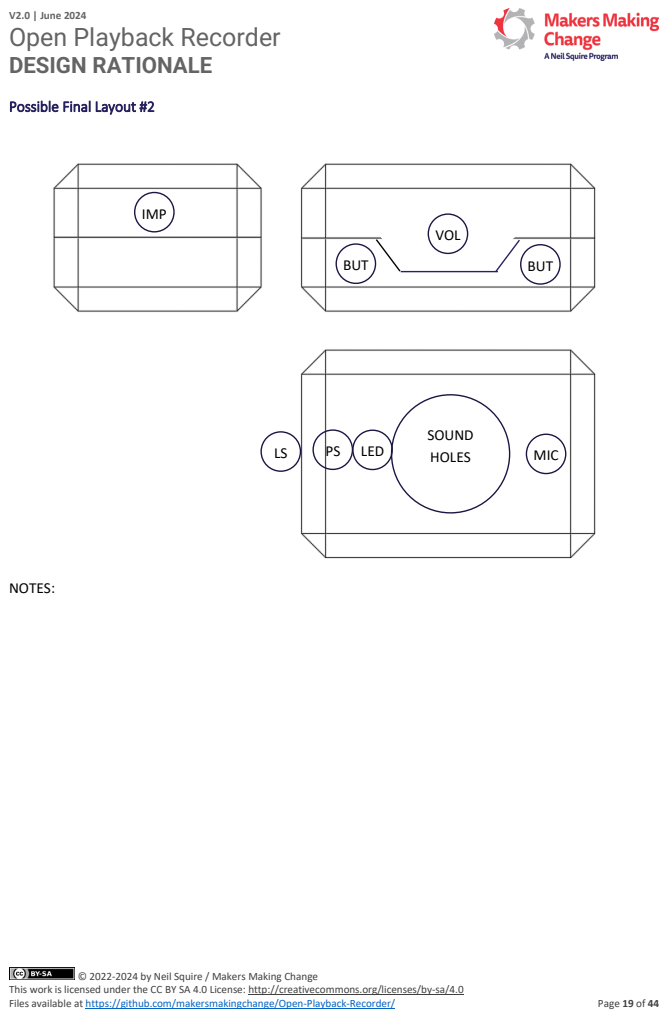
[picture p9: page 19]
Files available at https://github.com/makersmakingchange/Open-Playback-Recorder/; Page 19 of 44; NOTES:; SOUND; HOLES; MIC; IMP; BUT; VOL; LED

Possible Final Layout #2

## DESIGN RATIONALE

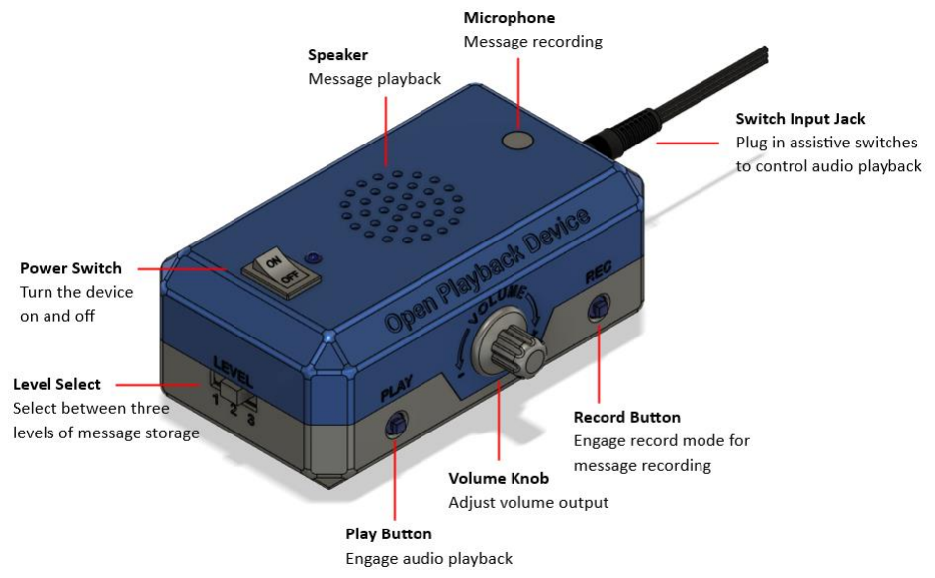
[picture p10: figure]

Files available at https://github.com/makersmakingchange/Open-Playback-Recorder/ | Page 20 of 44

## DESIGN RATIONALE

Files available at https://github.com/makersmakingchange/Open-Playback-Recorder/ | Page 21 of 44

### Sound Indicators

### V0.3 Feature Set

- Similar functionality to the MVP
- 3 level switch has been added to swap between 3 levels of message storage

### Device Naming

Existing Names:

- Big Mack
- Big Step-by-Step
- iTalk
- TalkingBrix
- QuickTalker

Possible Names:

- Open Playback Button
- Open Playback Switch
- Speech Generation Device
- Yak Back – Stephen
- Playback Parrot – Brad
- Record and Play
- Open Playback Device
- Open Playback Record
- Open Playback Recorder
- Multi-message Playback Recorder
- Open Record and Play
- Open Voice Recorder
- Open Audio Recorder
- Audio Record and Play

After running through the name generation exercise, the following names were chosen as possibilities.

- Playback Parrot
- Record and Play
- Command Chronicler
- Rewind Recorder

## DESIGN RATIONALE

Files available at https://github.com/makersmakingchange/Open-Playback-Recorder/ | Page 22 of 44

### Opportunities for Improvement

### Alterative Versions

- Current version focused on recreating the “Big Mack” experience
- One playback button
- Sequential lists of messages
- 3 level select

Full Feature Version
- Without concern for cost, a full feature version could eliminate some of the limitations of functionality.
- Features to add.
- Louder speakers
- Screen to make set up and operation easier
- Multiple Input Jacks
- Output Jacks

Inexpensive Version
- Instead of using a microcontroller to add functionality to the device, a cheaper rec/playback module could be used.
- Limited record time.
- Limited number of tracks.
- Use of audio output jack to eliminate cost of audio amp and speakers.

User Interface Changes
- Move recording/playback LED closer to the microphone/away from the power switch so it doesn’t look like a power indicator
- Potentially move level selection from being a slide switch to 3 LEDS and a button/switch to scan through them to give primary user control over level selection

Maker Experience Changes
- Make all connections between halves of the build in one spot/anchor everything to protoboard so joints don’t snap during assembly

### Questions for Clients

How long do the stored messages need to be?

- Big Mack max length = 2 minutes
- Big Mack Step by Step = 4 minutes
- Pet training buttons = 30 seconds

## DESIGN RATIONALE

Files available at https://github.com/makersmakingchange/Open-Playback-Recorder/ | Page 23 of 44

In what ways will this device be used? In what ways could multiple messages be used?

- Communication aid
- Sequential message storage: E.g., recording steps of a recipe
- Speak therapy: record and listen

Would mono cable input jacks be useful to the user?

- Input jack to allow playback activation from external switches
- Input jack to allow the Playback Button to be used as a switch for external devices

Power control integrated with volume knob or not?

- Does volume level need to be consistent?

### User Feedback

Status Light

Record Mode entered: Flashes red

Recording: Solid red

Playback: Green

## DESIGN RATIONALE

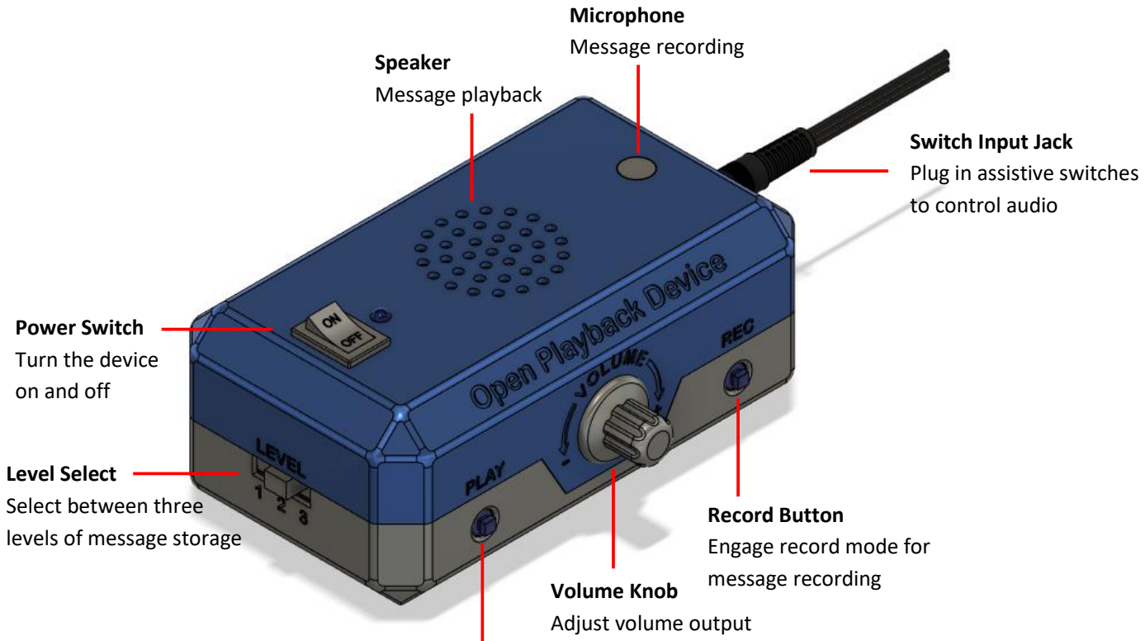
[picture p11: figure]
levels of message storage; Record Button Engage record mode for message recording Volume Knob; Adjust volume output; Speaker Message playback; Switch Input Jack Plug in assistive switches to control audio; Power Switch Turn the device on and off; Microphone Message recording

Files available at https://github.com/makersmakingchange/Open-Playback-Recorder/ | Page 24 of 44

### Opportunities for Improvement

- Add button to cover tactile buttons
- Fix spelling of Makers Making Change label
- Consider the positioning of record light (i.e., move away from power control to reduce confusion)
- Label microphone (either with words or symbol
- Wire spaghetti with components between top and bottom parts of enclosure

Play Button
Engage audio playback

Level Select
Select between three

## DESIGN RATIONALE

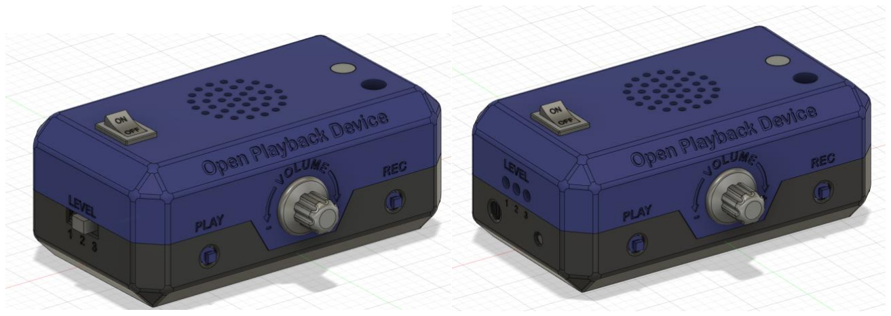
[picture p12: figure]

Files available at https://github.com/makersmakingchange/Open-Playback-Recorder/ | Page 25 of 44

V1.0

### Goals

- 3 level switch has been added to swap between 3 levels of message storage
- Slide switch or press button?
- Move record/play LED to more intuitive location so it doesn’t look like a power indicator
- More maker friendly build experience, make one set of cables between halves and reduce the “cheese pull” of wires connecting the two sides
- Consider replacing the microcontroller, SD card reader, and audio amplifier with the Adafruit Audio BFF (https://www.adafruit.com/product/5769)
- Miscellaneous CAD changes
- Add shadow lines
- Add a deboss around the LEDs/button/jack on the press button version
- Make the battery cover easier to remove
- Microphone cover

Level Selector
Two concepts were generated for the level selection. One used a three level slide switch and a resistor ladder connected to an analog input, and one used a push button in parallel with a switch jack to change the level.

The slide switch indicates the current level to the user with the physical position of the switch, and the push button indicates the position to the user using three LEDs, with one corresponding to each level.

Since the press button is in parallel with a switch jack, the level of the device can be changed by the primary user. Preliminary testing shows that the button does need a hardware debounce, most likely a lowpass filter.

Final selection was the button press, with a redesign of the UI to keep all controls on one side.

## DESIGN RATIONALE

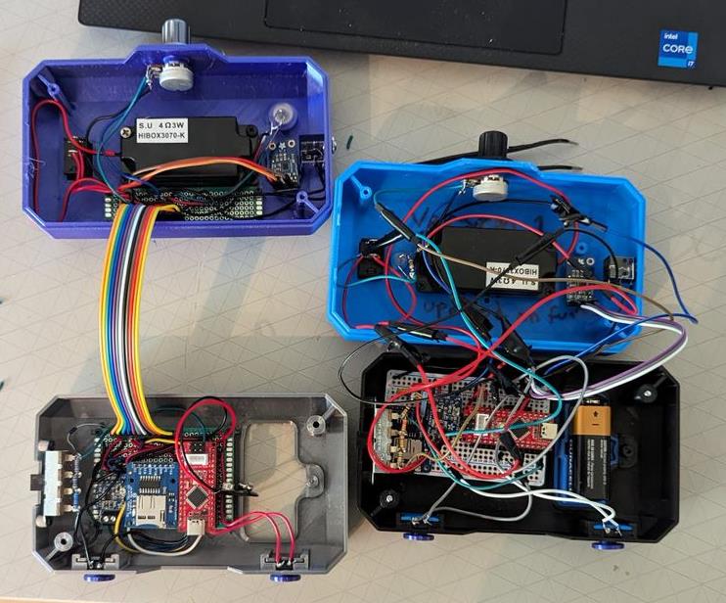
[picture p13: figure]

Files available at https://github.com/makersmakingchange/Open-Playback-Recorder/ | Page 26 of 44

Human Design Factor Update
The record and play LEDs were split into two LEDs to make it more clear which mode is active for colour blind users. All the LEDs and buttons were moved to the front side of the enclosure, with both jacks moved to the same side.

Maker Friendly Improvements
In the initial prototype, there were roughly 10 wires that connected the two halves. This made it difficult to assemble the two halves, as all the wires had to be inside the enclosure, and the act of opening or closing the enclosure put stress on the more fragile solder joints, repeatedly causing them to break during prototyping. A new design was created that used to protoboards to connect all the wires on each side, then connecting the two protoboards using a ribbon of breadboard wires. This is still very stiff, and there is still room for improvement finding a more flexible cable that allows the halves to close easier.

Alternative Audio Setup
Recently, Adafruit has come out with a device called the Audio BFF (https://www.adafruit.com/product/5769) board, which is a backpack style expander board for the QT Py or Xiao style microcontrollers. This board contains both a microSD card reader and a MAX98357 audio amplifier. This would replace the current microSD breakout board, and the audio amplifier. The BFF costs around 6 USD, while the microSD breakout and audio amplifier costs

## DESIGN RATIONALE

Files available at https://github.com/makersmakingchange/Open-Playback-Recorder/ | Page 27 of 44

around 15 CAD. The microcontroller would also need to be changed to one that matches the BFF footprint. This would cause issues with the number of pins needed for the device. It is possible to get GPIO pin extender, but that would bring the cost of the new solution to roughly the same price.

Current Setup | BFF Setup
Part | Price (USD) | Part | Price (USD)
Seeduino Nano (https://www.seeedstudio.com/Seeeduino-Nano-p-4111.html) | 7.60 | QT Py (https://www.adafruit.com/product/4600) | 7.50
MicroSD Breakout (https://www.adafruit.com/product/254) | 7.50 | Audio BFF (https://www.adafruit.com/product/5769) | 5.95
Audio Amplifier (https://www.adafruit.com/product/2130) | 3.95 | GPIO Extender (https://www.adafruit.com/product/4886) | 4.95
| | Stemma Cable (https://www.adafruit.com/product/4399) | 0.95
Total Price (USD) | 19.05 | Total Price (USD) | 19.35

### Changes

1. Finalize naming
2. ¼”-20 mount?
3. Secondary / Primary User Adjustable Levels?
- Add an input to switch between levels
- Add an indicator to indicate which level is selected
- Could be both tactile button and/or external switch input
4. Output Jack
a. What is the use case here?
5. Optimize assembly / enclosure to ease wiring
6. Swap from protobreadboard to protoboard

Final Changes
- Added jack/button for level selection
- Moved all buttons and lights to front face
- Moved all jacks to left side

### OFIs

- Look into rechargeable 9V batteries
- Look into adding an output jack
- May be able to improve BoM by ordering wire by the foot from digikey or mouser

## DESIGN RATIONALE

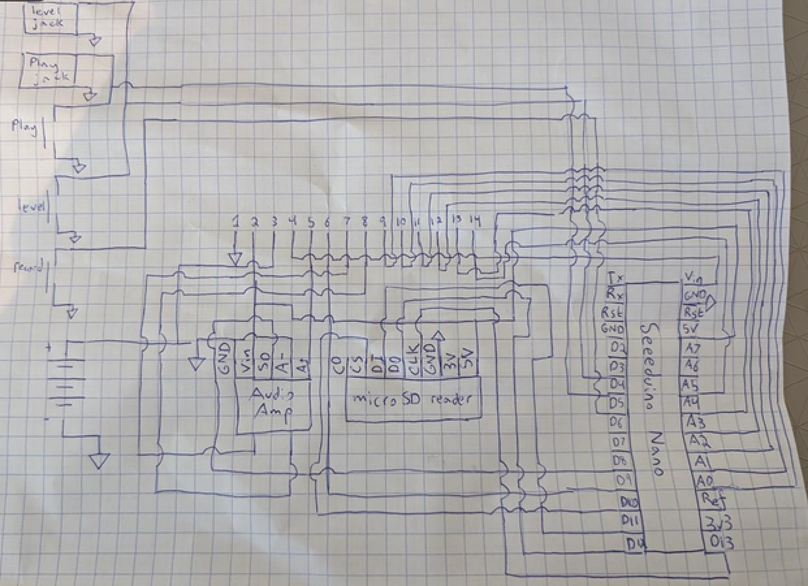
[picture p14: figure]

Files available at https://github.com/makersmakingchange/Open-Playback-Recorder/ | Page 28 of 44

### Final Schematic

## DESIGN RATIONALE

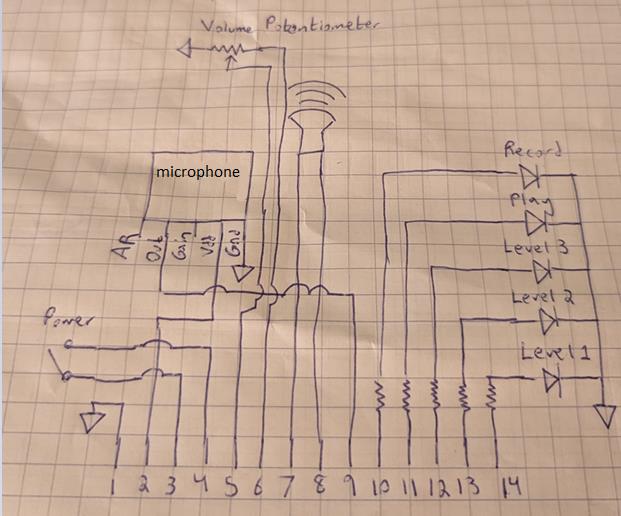
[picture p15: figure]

Files available at https://github.com/makersmakingchange/Open-Playback-Recorder/ | Page 29 of 44

## DESIGN RATIONALE

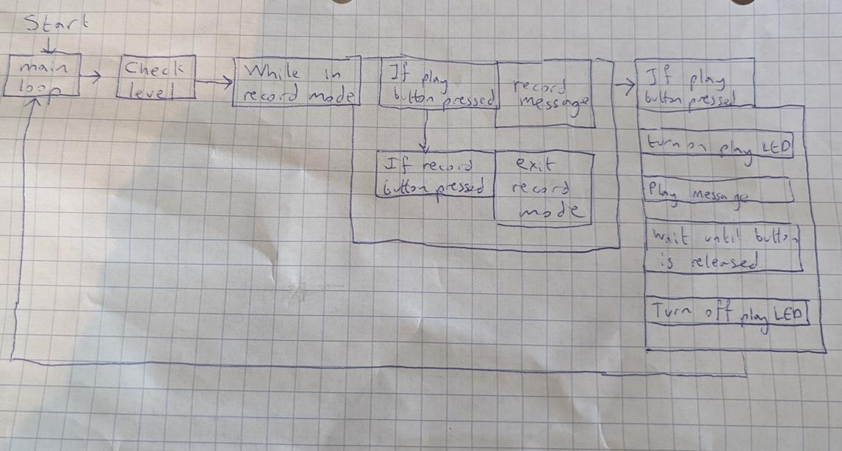
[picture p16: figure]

Files available at https://github.com/makersmakingchange/Open-Playback-Recorder/ | Page 30 of 44

### Code Architecture

V2.0
After building several Open Playback Recorders, it was decided that the build process took too long and had too many points of failure, which made it difficult for makers to build the device. It was decided to redesign the internals using a PCB to cut down on the cost and complexity of the device for makers.

### Project Charter

Purpose
- The Open Playback Recorder has proven to be a popular device, and there have already been over ten requests since the product was launched.
- Current protoboard and DuPont wire design takes ~8 hours to build, which is a significant barrier to makers

Objectives
- The objective of the project is to maintain the functionality of the Open Playback Recorder but improve the makeability by adding a PCB and re-evaluating the components to reduce opportunities for mistakes

## DESIGN RATIONALE

Files available at https://github.com/makersmakingchange/Open-Playback-Recorder/ | Page 31 of 44

What Success looks like
- Success would be an updated version of the Open Playback Recorder that maintains the same functionality, but with an improved makeability, with the possibility of a slightly modified form to accommodate the PCB and updated components

### Project Scope

Deliverables
- PCB Schematics for the updated design
- New BoM with the updated parts list
- Updated Maker Guide with the updated design
- Update the User Guide with updated photos and references if the form changes
- Update GitHub ReadMe
- Updated MMC Library Device page
- Document design update process in Design Rationale
- Updated CAD to accommodate the PCB

Requirements
- Build time must be cut in half from the protoboard version
- Cost must not be increased by more than 50 dollars
- Number of soldered joints/points of failure must be cut in half.
- User functionality must not be changed.

Out of Scope
- Any changes to the functionality are out of scope for the project. This project is strictly focused on improving the maker experience, and should have minimal to no effect on the user experience.

### PCB Layout

Limiting factors
- Eagle Design Space
- Max area of 80 cm²
- PCB Boardhouse pricing
- Gets more expensive if not in 10cmx10cm area
- Component spacing in the Open Playback Recorder
- Base
- Buttons on front, jacks on side
- Top
- LEDs and potentiometer on the front
- Microphone, power switch, speaker on top

## DESIGN RATIONALE

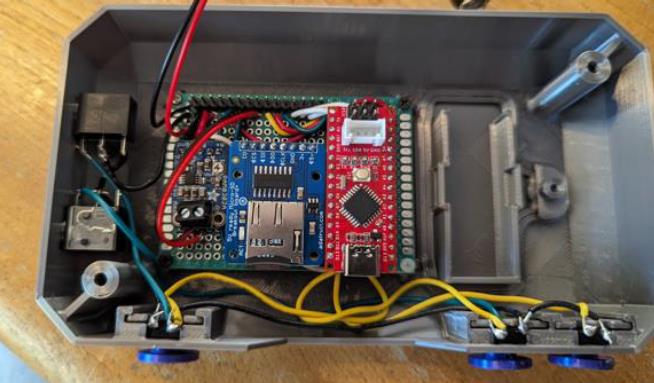
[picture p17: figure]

Files available at https://github.com/makersmakingchange/Open-Playback-Recorder/ | Page 32 of 44

Current Protoboard Layout
Base

In the top, there is a central protoboard that contains the microSD card, the speaker amplifier, and the microcontroller. The protoboard is mounted in the center of the base, with the buttons and jacks panel mounted and connected to the protoboard via wires.

Top

## DESIGN RATIONALE

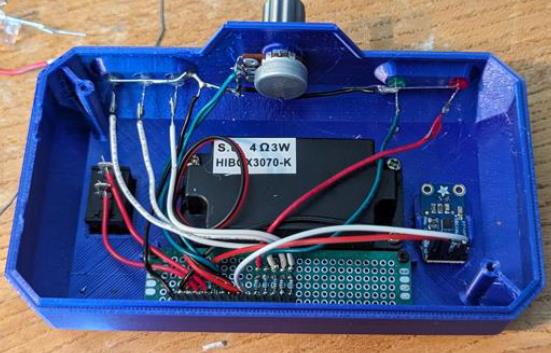
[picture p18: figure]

Files available at https://github.com/makersmakingchange/Open-Playback-Recorder/ | Page 33 of 44

In the top, there is a narrow protoboard for all the panel mount components to connect to. The only components mounted on the board are the resistors and the header that connects the two halves

Layout Options

One PCB
In this layout, there is only one PCB. Either all the components top and bottom are connected to the one PCB via wires like in the initial prototype, or only one of the protoboards is replaced with a PCB. Both options do not reduce the complexity of the device enough to warrant ordering a PCB.

Two PCBs
In the two PCB setup, each protoboard is replaced with a PCB

In the bottom, the protoboard is replaced with a single PCB. Given the size restrictions on designing and ordering PCBs, the overall size of the device would have to either shrinks significantly, the user interface components would have to be all moved to one corner of the board, or either the buttons or jacks remain panel mounted.

In the top, the protoboard would be replaced with a PCB. The DuPont header connection would be replaced with a ribbon cable for a more secure connection, with no risk of individual wires being crossed or coming undone. The PCB can either be mounted in the location of the current protoboard, or it can

## DESIGN RATIONALE

Files available at https://github.com/makersmakingchange/Open-Playback-Recorder/ | Page 34 of 44

be moved closer to the front of the device to allow the option of PCB mounting the LEDs and the potentiometer.

Three PCBs
In the three PCB setup, the top protoboard is replaced with a PCB, and the bottom protoboard is split into two separate PCBs for the buttons and the jacks.

In the bottom, the protoboard would be replaced with two PCBs, one with PCB mounted buttons, and one with panel mounted switch jacks. The other components that were mounted on the protoboard are split between the two PCBs. This allows the PCBs to slot in from the side from one direction, preventing assembly issues from slotting in components from multiple sides at once.

In the top, the protoboard would be replaced with a PCB. The DuPont header connection would be replaced with a ribbon cable for a more secure connection, with no risk of individual wires being crossed or coming undone. The PCB can either be mounted in the location of the current protoboard, or it can be moved closer to the front of the device to allow the option of PCB mounting the LEDs and the potentiometer.

More than three PCBs
The option of more than three PCBs will be explored if there are any serious roadblocks with the two or three PCB options that would require another PCB.

PCB Recommendation
Two PCBs strike a good balance between makeability and price. It allows for both protoboards to be replaced with PCBs and PCB mount most of the components, with the exception of the speaker. A third PCB in the base would allow more flexibility in assembling the device, but the cost of including a third PCB would outweigh the benefits.

### Component Review

Panel Mount vs PCB Mount
- PCB components reduce complexity, but can make assembly into the enclosure more difficult. (See Forest Hub for example)
- PCB components require the board to extend to the sides of the enclosure for user interface components
- Panel mount components make assembly easy, but need extra wire to get them to the board

Current User Interface Components
- Bottom
- Buttons
- Jacks
- Top

## DESIGN RATIONALE

Files available at https://github.com/makersmakingchange/Open-Playback-Recorder/ | Page 35 of 44
- Speaker
- Microphone
- Power Switch
- LEDs
- Potentiometer

Component Selection

User Interface
Top

Power Switch

- Current switch [Link] (https://www.mouser.ca/ProductDetail/E-Switch/RA11131123?qs=QtyuwXswaQhc6OwdGDJDiQ%3D%3D)
- Slide switch [Link] (https://www.digikey.ca/en/products/detail/c-k/OS102011MA1QN1/1981430)
- Currently mounted on the top, but power is coming from the base, and is consumed at the base. Would make sense for it to be at the bottom.

Speaker

- Wires come from the speaker, connect to the protoboard
- Solder to the protoboard
- Either continue to solder into the board, or add a terminal block to connect the wires to the PCB

LEDs

- Current LEDs can be used both as panel mount or PCB mount. If PCB mount, a spacer like the one used in the Forest Hub would be useful

Potentiometer

- Currently using a panel mounted logarithmic potentiometer [Link] (https://www.mouser.ca/ProductDetail/858-P160KNP0QC20A10K)
- PCB mounted 10kohm logarithmic potentiometer [Link] (https://www.digikey.ca/en/products/detail/cui-devices/PTN16-A10125K1A2/20380750)

Microphone

- Currently using electret microphone amplifier [Link] (https://www.adafruit.com/product/1713)
- Looked for stemma version to reduce soldering but not available

Bottom

Jacks

- Current selection [Link] (https://www.mouser.ca/ProductDetail/Switchcraft/35RAPC2AV?qs=I3kMT7EEIOWP5G1fR6CxcA%3D%3D)
- PCB mounted option [Link] (https://www.digikey.ca/en/products/detail/cui-devices/SJ1-3535NG/738699?s=N4IgTCBcDaIMIAUCMBaAzAVkwOQOIuwBEQBdAXyA)

## DESIGN RATIONALE

Files available at https://github.com/makersmakingchange/Open-Playback-Recorder/ | Page 36 of 44

Buttons

- Current selection is the button used in the raindrop switch [Link] (https://www.mouser.ca/ProductDetail/Omron-Electronics/B3F-5050?qs=dOLq8QE0Pqqk%2FO9x2OpTQw%3D%3D)
- PCB mounted button [Link] (http://www.digikey.ca/product-detail/en/wurth-electronics-inc/431256058736/431256058736-ND)

Internal
Microcontroller
- Needs to be 5v for some of the components
- Needs a large amount of pins
- Potential to get one with a built in SD card

MicroSD card reader

- Potential to combine the microSD card reader with the microcontroller
- Potential to

Speaker Amplifier

- Currently using the provided terminal block with wires going to the header. Possibility to replace the terminal block with the same headers used in the data lines providing the spacing is the same.

Battery

- CAD needs to be tweaked to add more tolerance to make the battery cover easier to remove
- Currently using a cable connected to the protoboard [Link] (https://www.mouser.ca/ProductDetail/Bud-Industries/HH-3449?qs=l8tafrjApPBvV0mmo%252BVZ5Q%3D%3D)
- Possibility to add terminals to the PCB and plug the battery directly into the PCB [Link] (https://thepihut.com/products/pcb-9v-connector-pair)

Part Recommendations
Top
- Microphone
- Continue to use the same microphone as before, but solder it directly to the PCB using headers.
- Speaker
- Continue to use the same speaker as before, soldered to the PCB or using terminal blocks
- LEDs
- Continue to use the same LEDs as before, but use a 3D printed spacer to get the LEDs in the correct orientation
- Potentiometer
- 10 kOhm PCB mounted logarithmic potentiometer

## DESIGN RATIONALE

Files available at https://github.com/makersmakingchange/Open-Playback-Recorder/ | Page 37 of 44
- If possible when doing the PCB layout, move to the bottom of the device to cut the required number of cables in the ribbon from 12 to 10
- Connection
- Ribbon cable for a secure connection and make it impossible for wires to get crossed
- Either 10 or 12 wire cable, depending if the potentiometer will fit on the bottom or not

Bottom

- Buttons
- PCB mounted to reduce number of wires and soldered connections.
- Capture the button covers internally to prevent them from falling off.
- Jacks
- PCB mounted to reduce number of wires and soldered connections.
- Move them closer to the front so they fit within the 100mm x 100mm area.
- MicroSD card reader
- Continue to use the same one as before, but move the port so the SD card is accessible by the secondary user
- Battery connection
- Keep existing connector
- PCB mount connectors are hard to reliably source on Digikey and Mouser
- Power switch
- Move to bottom of enclosure
- Slide switch to prevent bumping on or off
- PCB mount to simplify wiring
- Speaker amp
- Continue to use the same speaker amp as before, but replace the terminal block with additional headers to connect the output back into the PCB
- Microcontroller
- Continue to use the same microcontroller as before.
- Connection
- Ribbon cable for a secure connection and make it impossible for wires to get crossed
- Either 10 or 12 wire cable, depending if the potentiometer will fit on the bottom or not

### Proposed V2.0 Device Layout

In the proposed V2.0 layout, both protoboards are replaced with PCBs, and the overall size of the device is shrunk to accommodate the 100mmx100mm PCB restriction. All components with the exception of the speaker and battery connection are moved to through hole PCB mount. The power switch, and if possible, the potentiometer, are moved to the bottom PCB to reduce unnecessary crossings between the top and bottom. Since there will be PCB mounted components on 3 sides of the bottom PCB, the clamshell design will need to be modified for insertion of the PCB.

## DESIGN RATIONALE

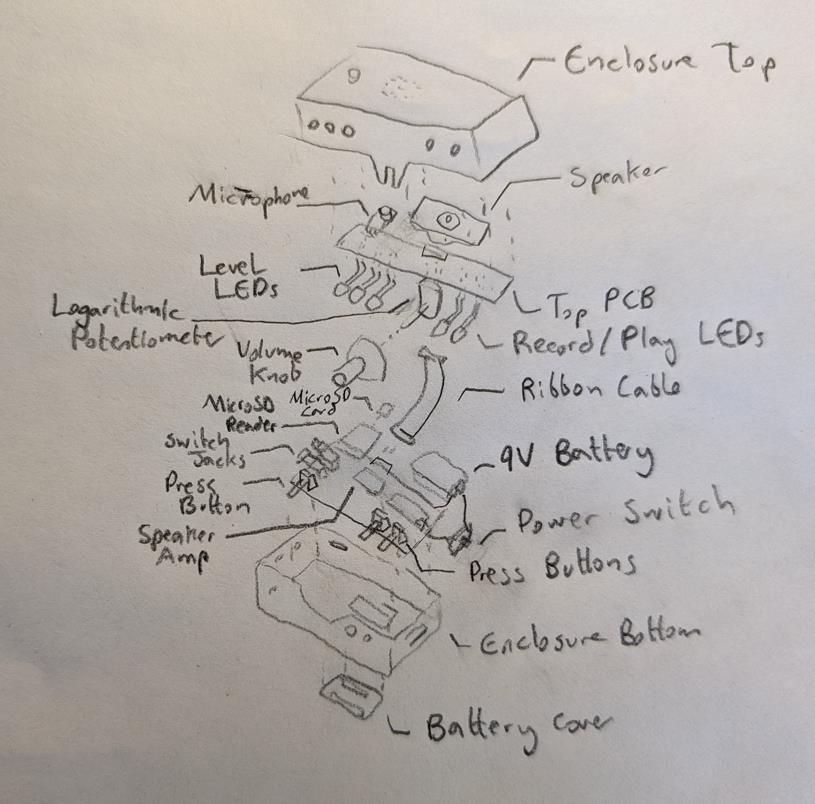
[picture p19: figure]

Files available at https://github.com/makersmakingchange/Open-Playback-Recorder/ | Page 38 of 44

The top PCB will contain the speaker connection, the 5 LEDs, the microphone, a ribbon cable connection, and potentially the potentiometer. The previous version had several connections that started and ended on the bottom board and just passed through the top, and part of the goal of the redesign is to minimize that.

The bottom board will have the jacks, buttons, power switch, microcontroller, battery connection, microSD card reader, speaker amp, and potentially the potentiometer. By making as many connections as possible on the PCB, it reduces the number of hand built wire traces to zero, and cuts the number of solder joints in half.

## DESIGN RATIONALE

Files available at https://github.com/makersmakingchange/Open-Playback-Recorder/ | Page 39 of 44

Updated Components

Component | Quantity | Price | Link
Jack | 2 | 1.98 (2.13) | Link (https://www.digikey.ca/en/products/detail/cui-devices/SJ1-3535NG/738699?s=N4IgTCBcDaIMIAUCMBaAzAVkwOQOIuwBEQBdAXyA)
Button | 3 | 0.82 (0.76) | Link (https://www.digikey.ca/en/products/detail/w%C3%BCrth-elektronik/431256058736/5209065?s=N4IgTCBcDaICwGYCMYCsA2ADKgHAdgXQFoA5AERAF0BfIA)
Power Switch | 1 | 0.89 (0.93) | Link (https://www.digikey.ca/en/products/detail/c-k/OS102011MA1QN1/1981430)
Potentiometer | 1 | 2.64 (2.13) | Link (https://www.digikey.ca/en/products/detail/cui-devices/PTN16-A10125K1A2/20380750)
10 wire ribbon cable | 1 | 1.82 () | Link (https://www.digikey.ca/en/products/detail/assmann-wsw-components/H3DDS-1006G/1218627)
10 wire ribbon cable connector | 2 | 0.86 () | Link (https://www.digikey.ca/en/products/detail/amphenol-cs-fci/86130101014345E1LF/7592367?s=N4IgTCBcDaIBwDYCMBmADEjGAsLsFYBRJAGQDEQBdAXyA)

### Updated Enclosure Design

Since the PCBs are so much smaller than the original enclosure, the fact that the buttons and jacks are PCB mount means that the enclosure must be redesigned around the PCBs. After the first draft of the PCBs were made, all the components were imported into Fusion and arranged in the most compact

## DESIGN RATIONALE

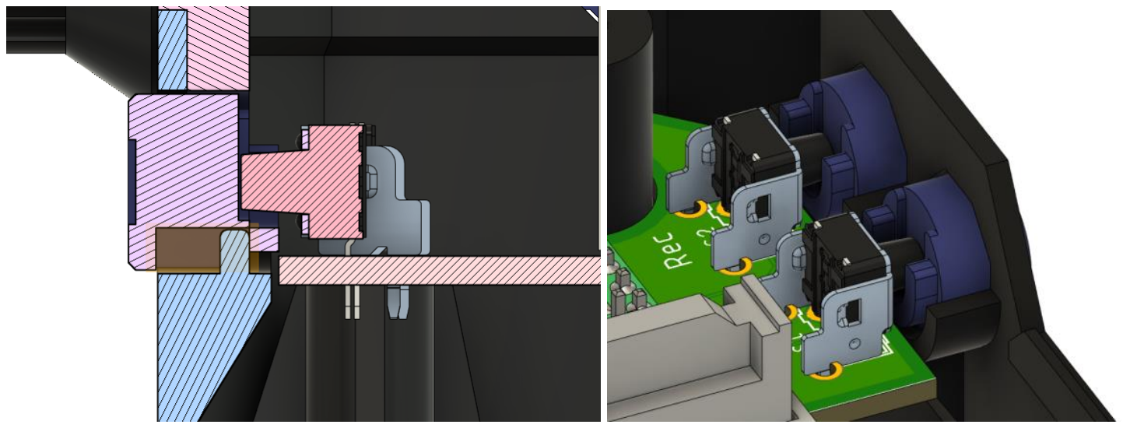
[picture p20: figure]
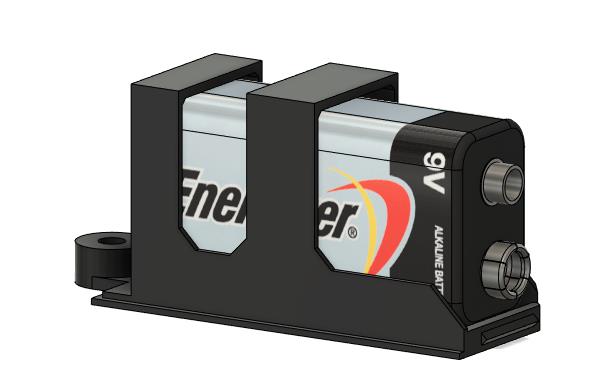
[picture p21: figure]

Files available at https://github.com/makersmakingchange/Open-Playback-Recorder/ | Page 40 of 44

manner possible. From here, the basic enclosure was modeled around the components. At this point, several changes to the PCBs were required to allow clearance for the screws holding the enclosure together, and to change the position of the microphone to make the enclosure more symmetric.

The design of the buttons and the battery holder was also overhauled from the initial version. The buttons on the initial enclosure were press fit onto the actual buttons, with a bit of hot glue holding them in place. This was fragile and prone to being knocked off, so the updated enclosure includes buttons that are inserted from the inside, and held in place by the PCB buttons after the PCB is inserted.

The battery holder was also redesigned, both to securely hold the battery so it can’t be shaken loose internally, and to allow the battery holder to more easily be removed from the enclosure with minimal force.

The LEDs used on the top circuit board need to be bent 90 degrees at a specific point to fit into the corresponding holes in the enclosure. In the past, 3D printed jigs have been used to bend components at a fixed point to eliminate the need to measure and guess. 3D printed spacers have also been used in the past to offset LEDs from the PCB. These two concepts were combined in this project to create a tiered spacer that allows the LEDs to be soldered to the board at the correct height, then bent using the spacer as a jig to get the correct angle and distances.

## DESIGN RATIONALE

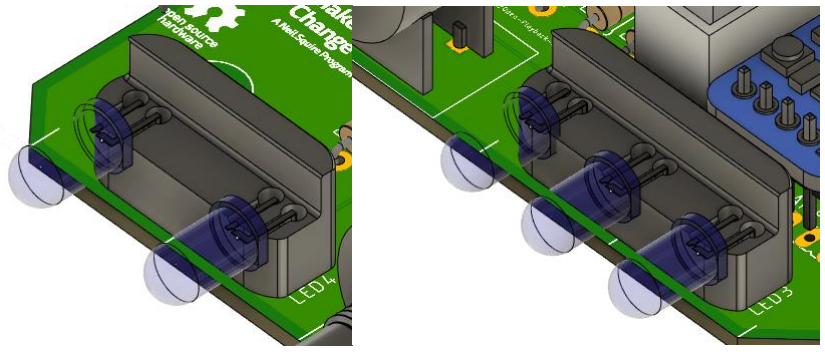
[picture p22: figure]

Files available at https://github.com/makersmakingchange/Open-Playback-Recorder/ | Page 41 of 44

### Initial PCB Design

The first PCB design designed alongside the new enclosure, and the PCBs and parts were ordered. Once everything arrived, the device was assembled using the previous code with no changes. The basic functionality of the device worked well, but there were three noticed issues that required a PCB rework.

The primary issue noticed was with the headers that connected the two halves of the device together. The actual headers were much larger than expected, and without a 3D model to incorporate them into the CAD, it went unnoticed that the headers would interfere with each other and the microcontroller. To fix this, in the next iteration of the PCBs the location of the header on the top PCB has been moved. Now that the header parts have arrived, they have been modeled and it has been verified that they will not interfere when assembled.

The second issue that was noticed was that the LED for level 3 was lighting when the device was in level 1, and vice versa. While this was an easy fix in software, since changes were already being made to the PCBs it was decided to swap the two LEDs to keep the software the same between the protoboard and PCB designs.

Finally, it was noticed that when a switch was connected to the Play jack, the level would also activate whenever the switch was pressed. This behavior stopped when a multimeter was used to measure the voltage on the input pin or when a 10k resistor was connected between the input pin and the 5V pin. This behavior seems like a floating input pin, but internal pullups have been enabled on all the microcontroller inputs. To solve this, optional pullup resistors were added to each of the microcontroller inputs to allow the maker to add resistors if the input is floating.

## DESIGN RATIONALE

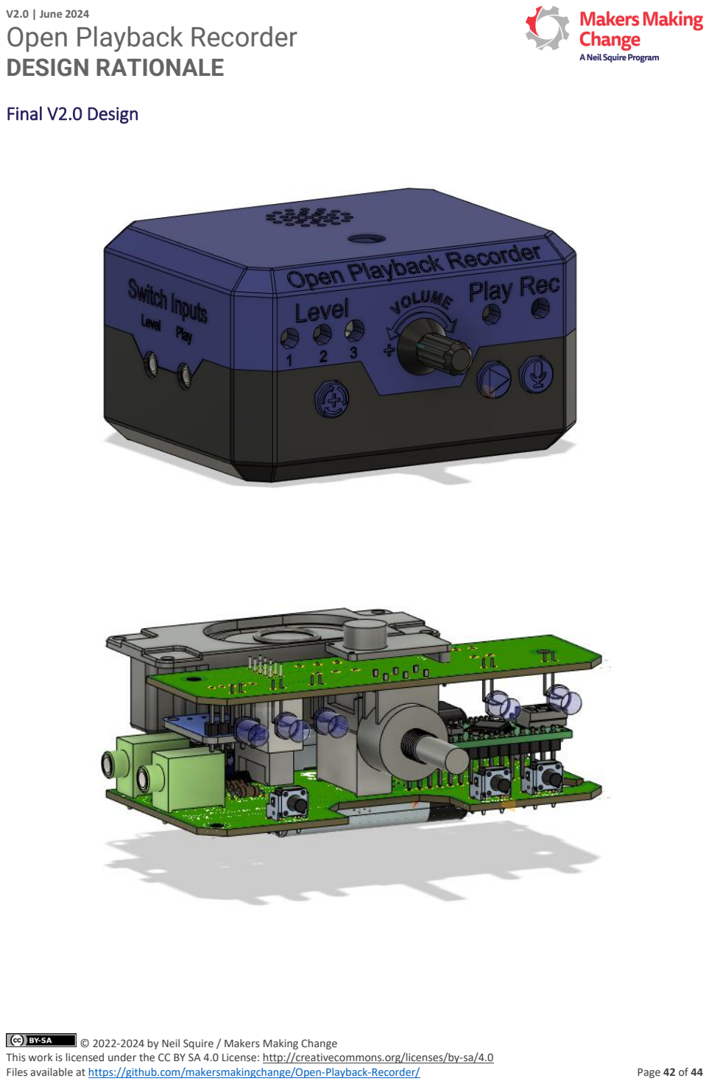
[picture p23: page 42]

Files available at https://github.com/makersmakingchange/Open-Playback-Recorder/ | Page 42 of 44

### Final V2.0 Design

## DESIGN RATIONALE

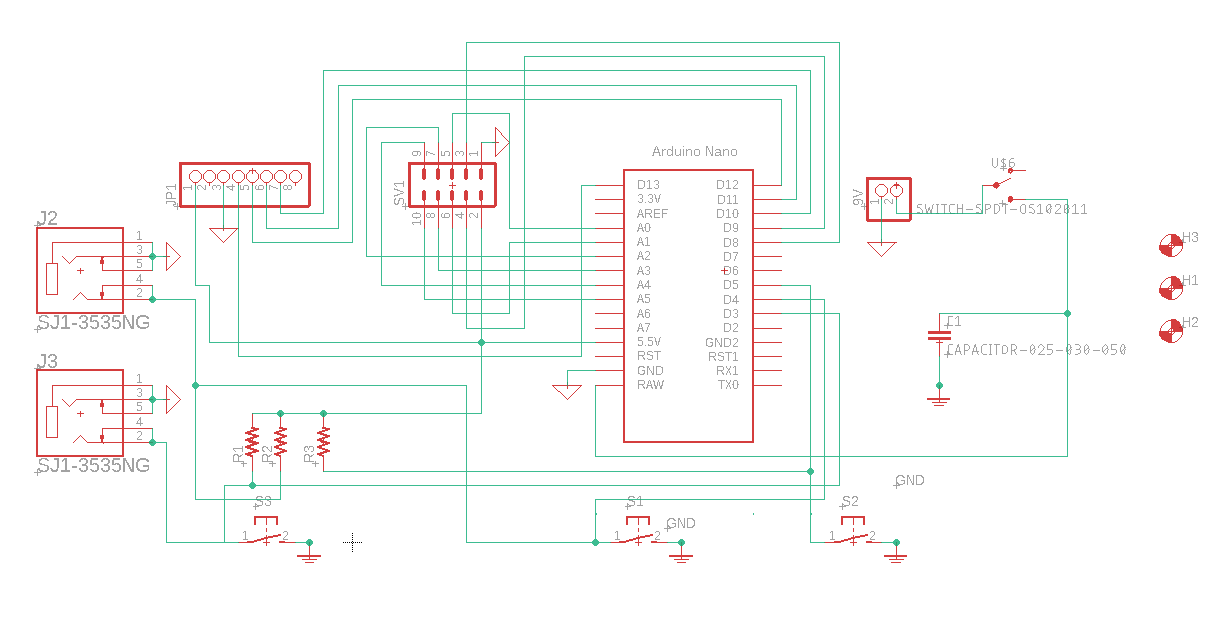
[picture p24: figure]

Files available at https://github.com/makersmakingchange/Open-Playback-Recorder/ | Page 43 of 44

### V2.0 Testing and Validation

V2.0 Internal Testing
Test pull-up resistors and input ghosting

Input Ghosting
When an assistive switch is connected to the play jack and it is pressed, the level switch will sometimes also activate, with nothing connected to the level jack and the level button not being pressed. There is already an internal pullup resistor on both the play and level input pins. On the first prototype PCB, this was eliminated by soldering a 10k resistor between the level pin and the 5V pin on the microcontroller.

On the second iteration of the board, a footprint was added for the pullup resistors, however this made them less effective, with the ghost input happening roughly half the time.

## DESIGN RATIONALE

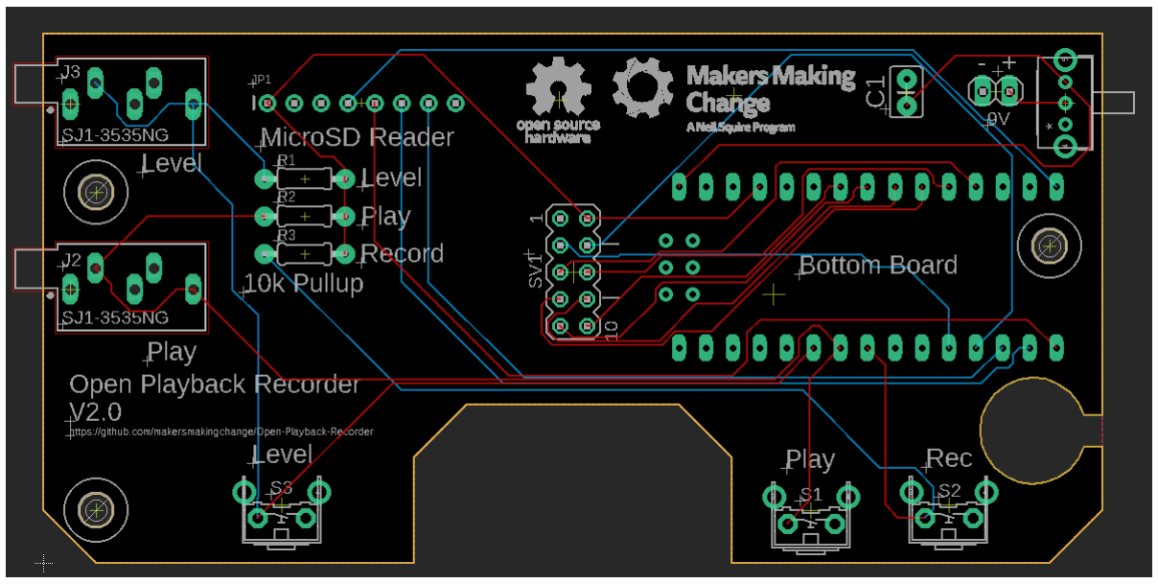
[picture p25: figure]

Files available at https://github.com/makersmakingchange/Open-Playback-Recorder/ | Page 44 of 44

After reviewing the software for the OPR, it was found that the fact that the level switch input was an interrupt was causing issues. Since interrupts cannot trigger within an Interrupt Service Routine(ISR), things such as timers and delays cannot be used within the ISR for the level change. This makes it difficult to debounce the level switch in software since any debouncing after the ISR would simply be interrupted when the ISR is triggered again by the bouncing. Since the level change is only needed in the main loop and is not used while playing or recording messages, the interrupt was removed and an if statement added to the main loop to poll the state of the level pin. This change solved both the input ghosting and the switch bouncing issue with no changes needed on the PCB.

V2.0 User Testing
Test if having the microcontroller and microSD card accessible is a useful addition

Test to make sure that no functionality was lost

V2.0 Build Testing
Test maker guide to verify the instructions are clear, easy to understand, and have no errors.

### OFIs for V2.1

- Add sliding covers for microcontroller, power switch, and the microSD card
- Get OSHWA certification
- Possible to lose the microSD card in the enclosure when removing it

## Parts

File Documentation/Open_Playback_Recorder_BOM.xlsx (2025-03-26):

Open Playback Recorder |  |  |  |  |  |  |  | Unit Cost | Total Cost | Total Print time (hr) | Total filament (g)
Version: V2.0 |  | Last Updated: Jun 21, 2024 |  |  |  |  |  | $93.40 | $112.38 | 3.23 | 90
Commercial Parts
ID | Part Name | Part Type | QTY | QTY/PKG | $/PKG | PKG QTY | $/Unit | Extended | Total | Link
102010268 | Micro Controller (Seeeduino Nano) | Electrical | 1 | 1 | $10.99 | 1 | $10.99 | $10.99 | $10.99 | https://www.digikey.ca/en/products/detail/seeed-technology-co-ltd/102010268/10290292
2130 | Audio Amplifier (Pam8302) | Electrical | 1 | 1 | $6.09 | 1 | $6.09 | $6.09 | $6.09 | https://www.digikey.ca/en/products/detail/adafruit-industries-llc/2130/5761279
3351 | Mono Speaker (4Ω 3W ) | Electrical | 1 | 1 | $6.09 | 1 | $6.09 | $6.09 | $6.09 | https://www.digikey.ca/en/products/detail/adafruit-industries-llc/3351/6612456
PTN16-A10125K1A2 | Audio Potentiometer | Electrical | 1 | 1 | $3.08 | 1 | $3.08 | $3.08 | $3.08 | https://www.digikey.ca/en/products/detail/cui-devices/PTN16-A10125K1A2/20380750
254 | Micro SD Reader | Electrical | 1 | 1 | $10.85 | 1 | $10.85 | $10.85 | $10.85 | https://www.digikey.ca/en/products/detail/adafruit-industries-llc/254/5761230
5249 | Micro SD Card | Electrical | 1 | 1 | $7.86 | 1 | $7.86 | $7.86 | $7.86 | https://www.digikey.ca/en/products/detail/adafruit-industries-llc/5252/15841478
1713 | Microphone (MAX9814) | Electrical | 1 | 1 | $11.50 | 1 | $11.50 | $11.50 | $11.50 | https://www.digikey.ca/en/products/detail/adafruit-industries-llc/1713/4990777
B3F-3152 | Buttons (B3F-3152) | Electrical | 3 | 1 | $0.51 | 1 | $0.51 | $1.53 | $1.53 | https://www.digikey.ca/en/products/detail/omron-electronics-inc-emc-div/B3F-3152/31741
OS102011MA1QS1 | Toggle Switch | Electrical | 1 | 1 | $0.65 | 1 | $0.65 | $0.65 | $0.65 | https://www.digikey.ca/en/products/detail/c-k/OS102011MA1QS1/1981431
SJ1-3535NG | 3.5 mm Mono Jack | Electrical | 2 | 1 | $2.31 | 1 | $2.31 | $4.62 | $4.62 | https://www.digikey.ca/en/products/detail/cui-devices/SJ1-3535NG/738699
EALP05RDHRA2 | Red LED | Electrical | 1 | 1 | $0.63 | 1 | $0.63 | $0.63 | $0.63 | https://www.digikey.ca/en/products/detail/everlight-electronics-co-ltd/EALP05RDHRA2/5142171
151051VS04000 | Green LED | Electrical | 1 | 1 | $0.40 | 1 | $0.40 | $0.40 | $0.40 | https://www.digikey.ca/en/products/detail/w%C3%BCrth-elektronik/151051VS04000/4490015
OVLFB3C7 | Blue LED | Electrical | 3 | 1 | $0.40 | 3 | $0.40 | $1.20 | $3.60 | https://www.digikey.ca/en/products/detail/w%C3%BCrth-elektronik/151051BS04000/4490009
MFR-25FRF52-2K | Resistor (2k Ω) | Electrical | 5 | 1 | $0.15 | 1 | $0.15 | $0.75 | $0.75 | https://www.digikey.ca/en/products/detail/yageo/MFR-25FRF52-2K/14920
PPTC051LFBN-RC | 5 pin header | Electrical | 1 | 1 | $0.70 | 1 | $0.70 | $0.70 | $0.70 | https://www.digikey.ca/en/products/detail/sullins-connector-solutions/PPTC051LFBN-RC/807239
PPTC151LFBN-RC | 15 pin header | Electrical | 2 | 1 | $1.44 | 1 | $1.44 | $2.88 | $2.88 | https://www.digikey.ca/en/products/detail/sullins-connector-solutions/PPTC151LFBN-RC/810153
A1604 BK210J | 9V Battery | Electrical | 1 | 1 | $9.62 | 1 | $9.62 | $9.62 | $9.62 | https://www.digikey.ca/en/products/detail/duracell-industrial-operations-inc/9V/21259959
C315C104M5U5TA | Capacitor | Electrical | 1 | 1 | $0.47 | 1 | $0.47 | $0.47 | $0.47 | https://www.digikey.ca/en/products/detail/kemet/C315C104M5U5TA/817927
 | T-Nut | Mechanical | 1 | 50 | $16.92 | 1 | $0.34 | $0.34 | $16.92 | https://www.amazon.ca/gp/product/B07NCXNKJR
HH-3449 | 9V Battery Clip | Electrical | 1 | 1 | $0.76 | 1 | $0.76 | $0.76 | $0.76 | https://www.digikey.ca/en/products/detail/keystone-electronics/232/303804
6005 | #4 Sheet Metal Screw | Mechanical | 11 | 1 | $0.60 | 1 | $0.60 | $6.60 | $6.60 | https://www.digikey.ca/en/products/detail/serpac/6005/307599
H3DDS-1006G | Ribbon Cable | Electrical | 1 | 1 | $1.82 | 1 | $1.82 | $1.82 | $1.82 | https://www.digikey.ca/en/products/detail/assmann-wsw-components/H3DDS-1006G/1218627
86130101014345E1LF | Ribbon Cable Header | Electrical | 2 | 1 | $0.86 | 1 | $0.86 | $1.72 | $1.72 | https://www.digikey.ca/en/products/detail/amphenol-cs-fci/86130101014345E1LF/7592367
 |  |  |  |  |  |  | $0.00 | $0.00 | $0.00
3D Printed Parts ESTIMATED PRICING USING 1KG ROLL COST: |  | $25.00
ID | Part | Material | QTY | Mass (g) / Unit | Time / Unit |  | Print Time (Min) | Estimated Price |  | Link
 | Base | PLA | 1 | 40 | 70 |  | 70 | $1.00
 | Battery Cover | PLA | 1 | 5 | 16 |  | 16 | $0.12
 | 3 LED Spacer | PLA | 1 |  | 6 |  | 6
 | 2 LED Spacer | PLA | 1 | 1 | 5 |  | 5 | $0.03
 | Level Button | PLA | 1 | 1 | 3 |  | 3 | $0.03
 | Lid | PLA | 1 | 39 | 79 |  | 79 | $0.97
 | Play Button | PLA | 1 | 1 | 3 |  | 3 | $0.03
 | Record Button | PLA | 1 | 1 | 3 |  | 3 | $0.03
 | Volume Knob | PLA | 1 | 2 | 9 |  | 9 | $0.05
Custom Printed Circuit Board (PCB)
ID | Part |  | QTY | QTY/PKG | $/PKG |  | Link
 | Open Playback Recorder Top PCB |  | 1 | 5 | $5.00 |  | https://www.pcbway.com/
 | Open Playback Recorder Bottom PCB |  | 1 | 5 | $5.00 |  | https://www.pcbway.com/
 | PCB shipping |  | 1 | 1 | $25.00
Tools for Assembly
 | Soldering Iron
 | 60Pb/40Tn Solder Wire
 | Needle Nose Pliers
 | Flush Cutters
 | Super Glue
 | Desolder Pump (Optional)
Alternatives (if there are other sources for some parts link them below)
ID | Part and description | Link |  |  |  |  |  |  |  | Link
2130 | Audio Amplifier (Pam8302) | https://www.adafruit.com/product/2130
4445 | Mono Speaker (4Ω 3W ) | https://www.adafruit.com/product/4445
254 | Micro SD Reader | https://www.adafruit.com/product/254
5250 | Micro SD Card | https://www.adafruit.com/product/5250
1713 | Microphone (MAX9814) | https://www.adafruit.com/product/1713
1119 | Buttons (B3F-5050) | https://www.adafruit.com/product/1119
4361 | 3.5 mm Mono Jack | https://www.adafruit.com/product/4361
4294 | Resistor (1k Ω) | https://www.adafruit.com/product/4294
2671 | Male Through Hole Header | https://www.adafruit.com/product/2671
598 | Female Through Hole Header | https://www.adafruit.com/product/598
80 | 9V Battery Clip | https://www.adafruit.com/product/80
301 | Blue LED | https://www.adafruit.com/product/301
298 | Green LED | https://www.adafruit.com/product/298
299 | Red LED | https://www.adafruit.com/product/299

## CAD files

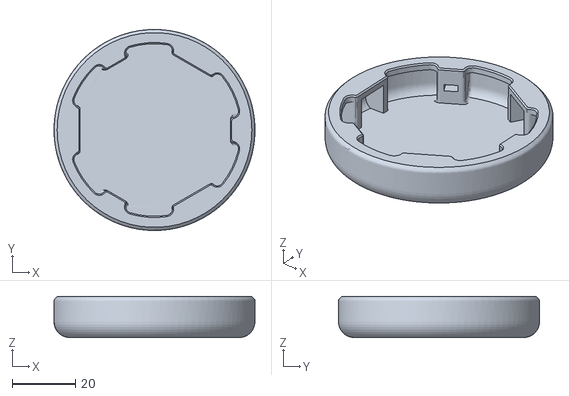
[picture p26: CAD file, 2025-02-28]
Build_Files/3D_Printing_Files/Custom Interact Toppers/Interact Topper - Play.stl
63.5 x 63.5 x 13.0

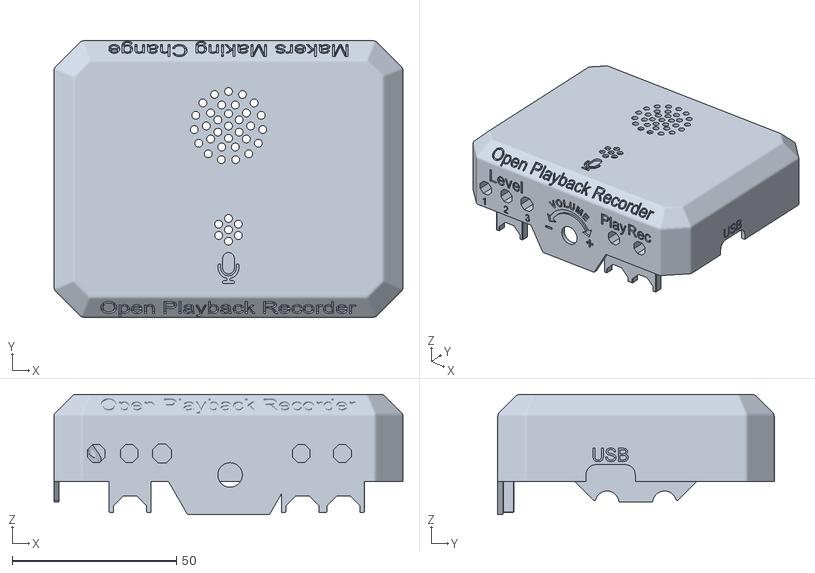
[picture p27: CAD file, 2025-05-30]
Build_Files/3D_Printing_Files/Lid.stl
106.4 x 84.3 x 36.6

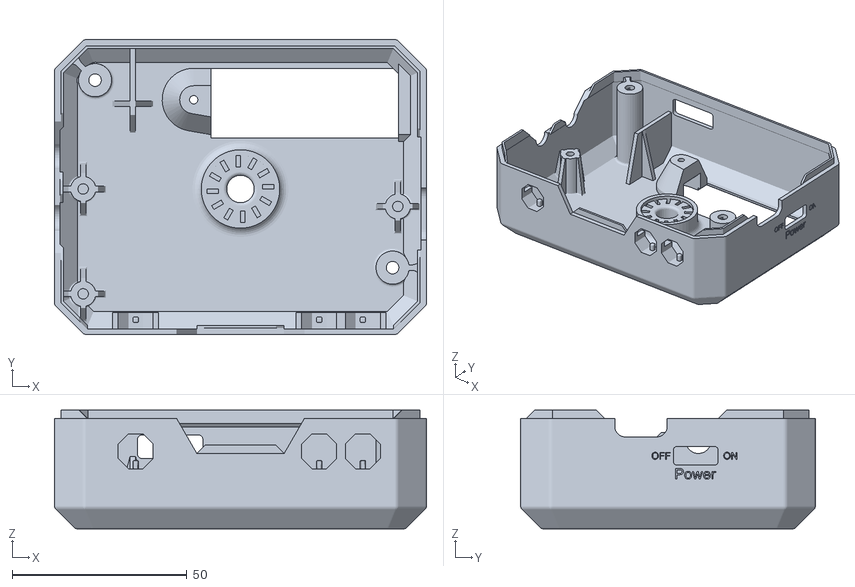
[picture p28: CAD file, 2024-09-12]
Build_Files/3D_Printing_Files/Base.stl
106.4 x 84.3 x 34.0

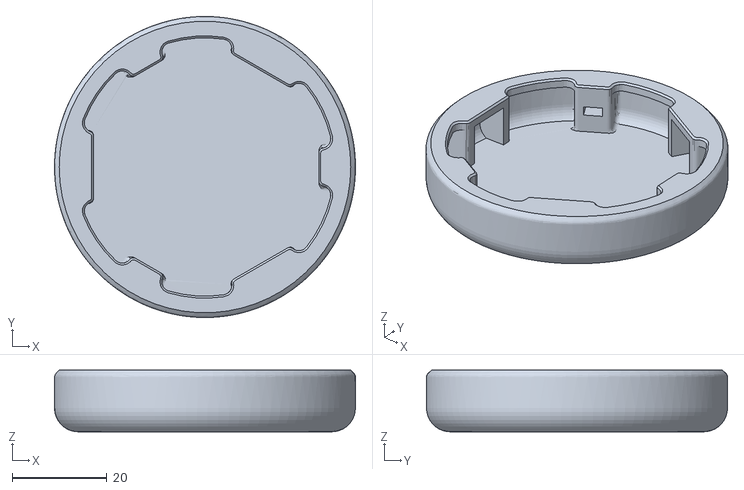
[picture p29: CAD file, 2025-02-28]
Build_Files/3D_Printing_Files/Custom Interact Toppers/Interact Topper - Level.stl
63.5 x 63.5 x 13.0

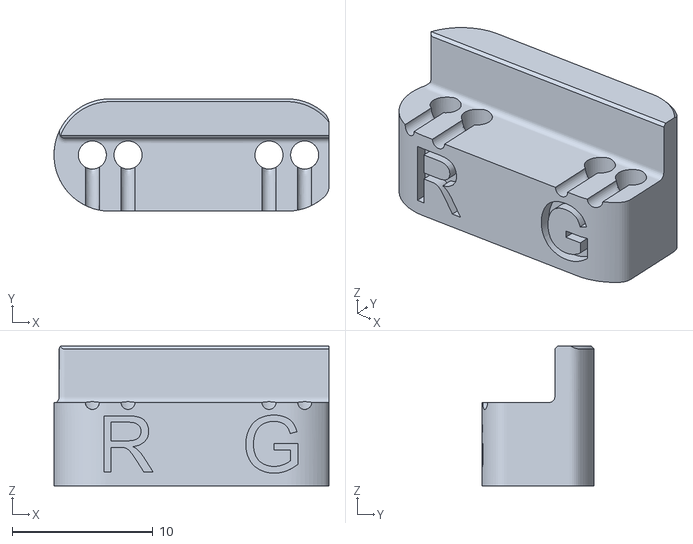
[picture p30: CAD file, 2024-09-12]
Build_Files/3D_Printing_Files/2 LED Spacer.stl
19.6 x 8.00 x 9.93

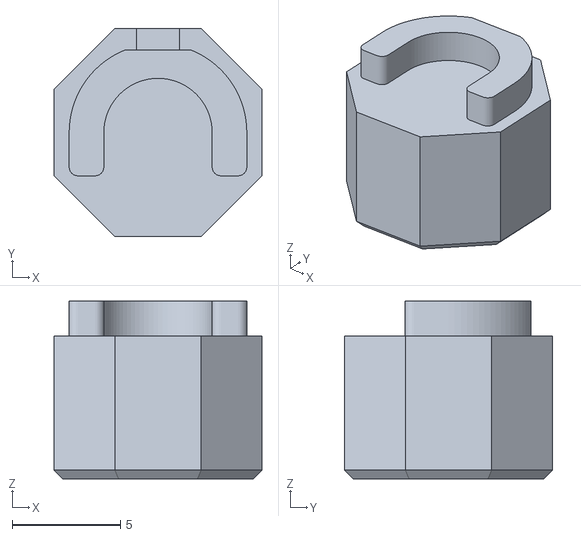
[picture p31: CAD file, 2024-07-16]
Build_Files/3D_Printing_Files/Record Button.stl
9.60 x 9.60 x 8.20

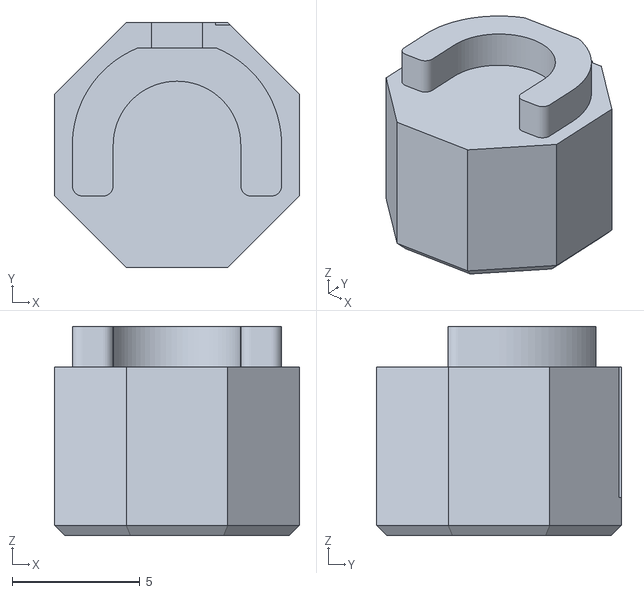
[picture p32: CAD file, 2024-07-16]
Build_Files/3D_Printing_Files/Level Button.stl
9.60 x 9.60 x 8.20

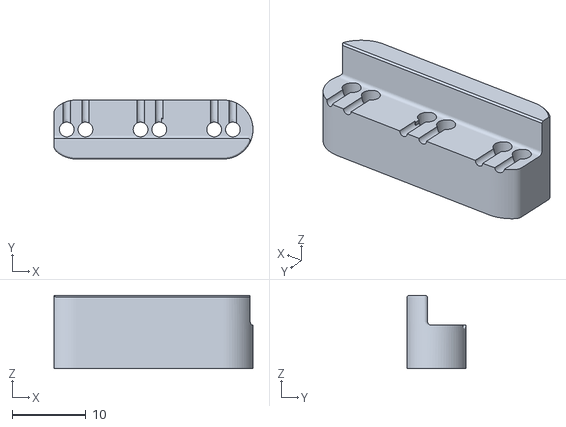
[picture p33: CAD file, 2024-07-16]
Build_Files/3D_Printing_Files/3 LED Spacer.stl
27.0 x 8.00 x 9.93

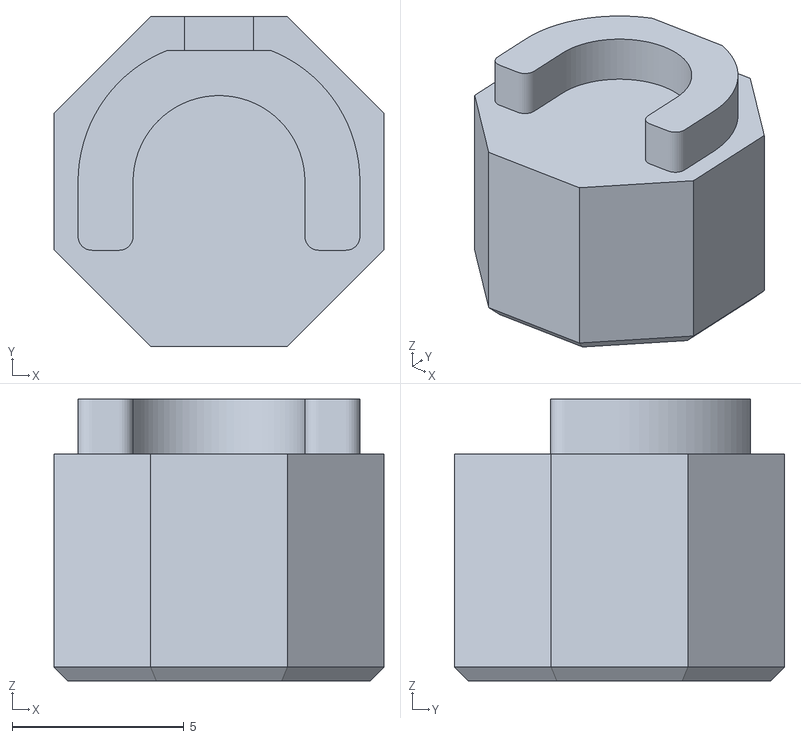
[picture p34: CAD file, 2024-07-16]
Build_Files/3D_Printing_Files/Play Button.stl
9.60 x 9.60 x 8.20

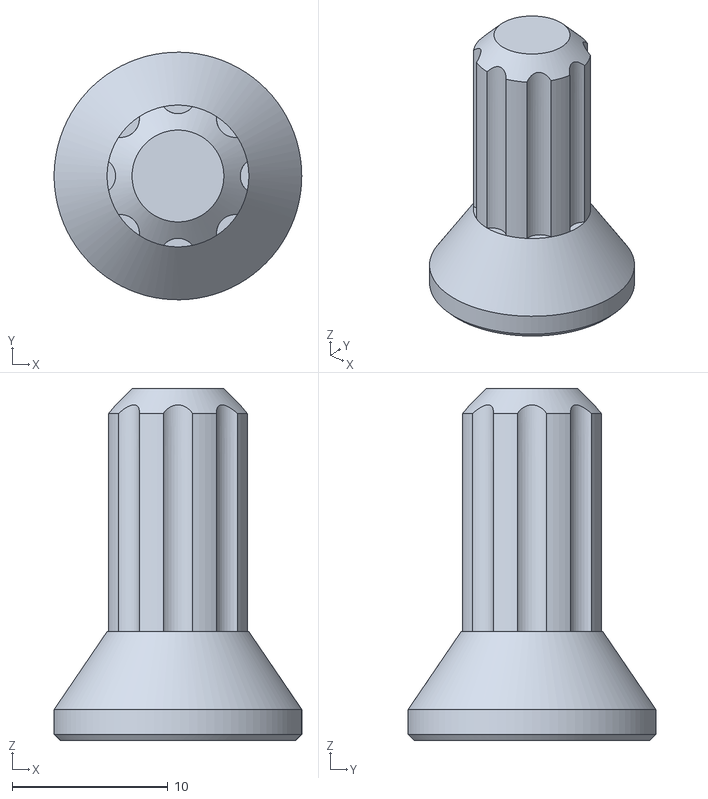
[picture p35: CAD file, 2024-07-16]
Build_Files/3D_Printing_Files/Volume Knob.stl
15.9 x 15.9 x 22.6

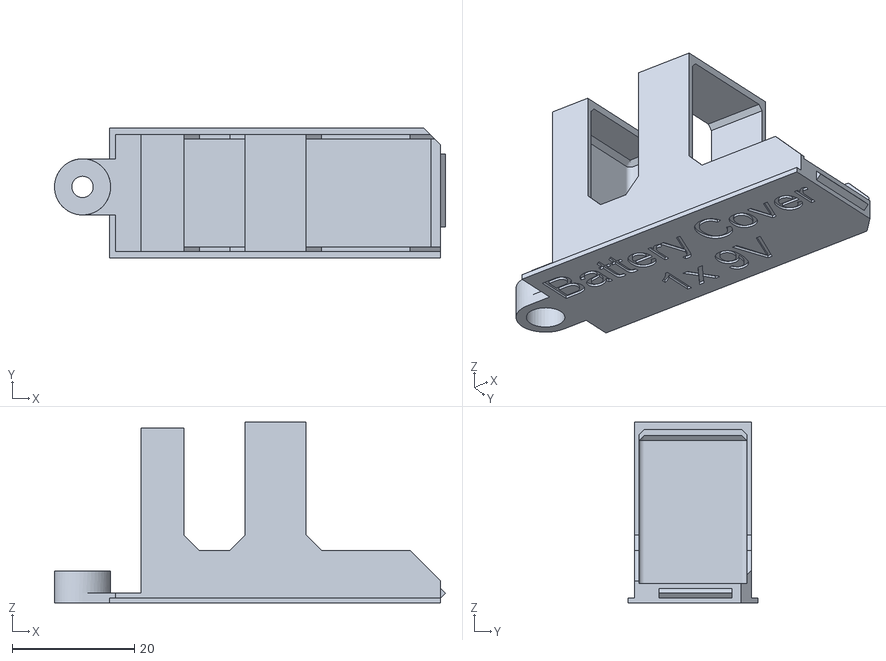
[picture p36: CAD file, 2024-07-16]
Build_Files/3D_Printing_Files/Battery Cover.stl
64.0 x 21.2 x 29.6

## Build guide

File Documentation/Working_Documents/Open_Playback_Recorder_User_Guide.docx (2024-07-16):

## Introduction

The Open Playback Recorder is an open-source device that can record three lists of voice messages that its user can playback via the trigger of an accessible button connected through a 3.5 mm mono jack. It aims to assist users with communication difficulties by giving them alternative methods to engage in conversation. This device has functionality like AbleNet’s Big Mack or Step by Step.

## Features

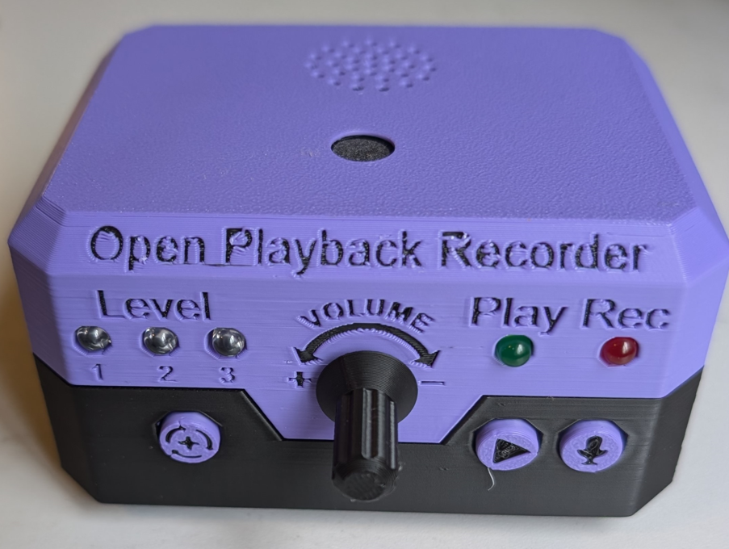
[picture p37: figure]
Open Playback Recorder with the buttons, LEDs, and volume knob labeled

Volume Knob

Play Button

Level button

Record Button

Record LED LEDs

Play LED

Level LEDs

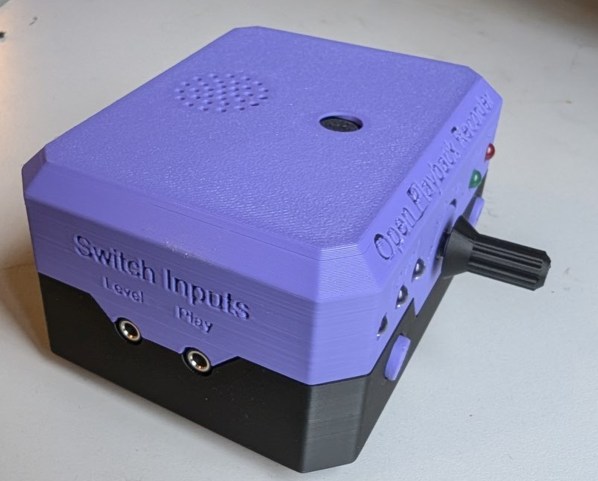
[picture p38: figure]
Open Playback Recorder with the speaker, microphone, level jack, and play jack labeled
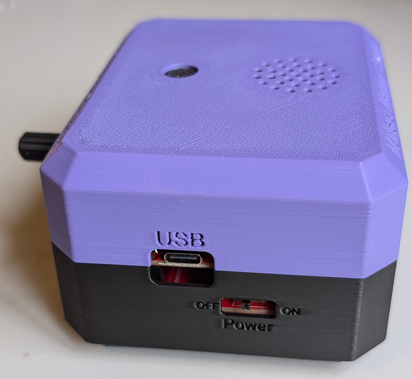
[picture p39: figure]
Open Playback Recorder with USB port and power switch labeled

USB Port

Power Switch

Level Jack

Play Jack

Speaker

Microphone

## Usage

### Setup

Connect two assistive switches, one to the jack labeled PLAY, and one to the jack labeled LEVEL.

### Power On

To power on the device, toggle the switch on the side of the device from OFF to ON.

The device can also be power through the USB port on the side of the device without needing a battery.

### Message Recording

To record one or more messages, the device needs to be in Record Mode. The device will record messages to the currently selected level.

Step 1. To engage “Record Mode” hold down the REC button for 2 seconds. When Record Mode is engaged, the REC LED will turn red and remain solid.

Note: When Record Mode is engaged, all previous messages on that level will be erased.

Step 2. To start message recording, press and hold the PLAY button or assistive switch connected to the play jack. The REC LED will flash red. Record the message into the microphone and release the button to end and save the message. The RED LED will once again turn red and remain solid.

Step 3. To record additional messages, repeat Step 2.

Note: These messages will later by played back in the same order they were recorded.

Step 4. When the desired messages have been recorded, press the REC button to exit Record Mode. The red REC LED will turn off.

### Message Playback

To play back a message, press an assistive switch connected to the play jack. This will play a message from the current recording level. The play button on the device itself will also allow a secondary user to play a message. Continuing to press the button will cycle through all the messages on that level.

To change the message level, press an assistive switch connected to the level jack. The level shift button on the device will also allow a secondary user to change the message level. The current level will be indicated by the three blue LEDs on the left side of the device.

## Compatibility

The device is compatible with any 3.5mm assistive switch

## Specifications

Weight | 250 grams
Length | 105 mm
Width | 85 mm
Height | 60 mm
Audio Recording Length | No limit, all recordings must fit in 512 MB, or roughly 500 minutes.
Assistive Switch Inputs | 2
Battery Type | 9V

## Maintenance

### Changing The Battery

To replace the 9V battery, use a Philips screwdriver to remove the screw holding the battery holder in place. Remove the battery holder, and remove the battery from the slot. A new battery can be can be inserted into the holder and the battery holder can then be put back into the device and secured with the screw.

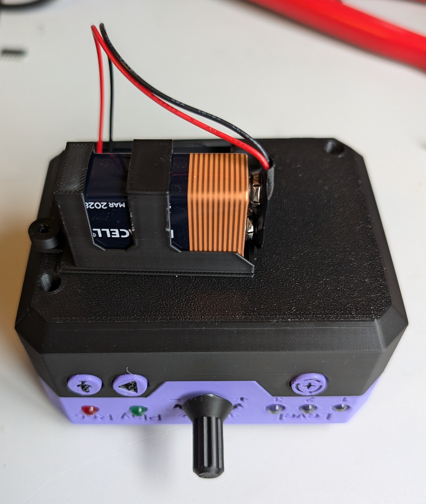
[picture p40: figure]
The Open playback recorder with the battery compartment opened to change the battery

## Cleaning

To clean the device, wipe down the outside with a damp cloth or cleaning wipes. Do not get the internal electronics wet.

## Troubleshooting

### Noises from the speaker / Not playing audio messages

If the speaker starts making unwanted noises while in REC / PLAY modes or messages do not play during message playback, this can be a sign that the battery is low on power. Follow instructions in the maintenance section to replace the battery.

### Device power cycles/resets when volume is too high

If the device power cycles or resets when the volume is set too high, this is a sign that the battery cannot provide enough current. This issue was noticed when using a Samxieng PowerfulCell 9V battery, and was solved by changing to a Duracell 9V battery.

© 2022-2024 by Neil Squire. This work is licensed under the CC BY SA 4.0 License: http://creativecommons.org/licenses/by-sa/4.0 Files available at https://github.com/makersmakingchange/Open-Playback-Recorder Page 2 of 3

V2.0 | JUNE 2024 Open Playback Recorder user Quick Guide

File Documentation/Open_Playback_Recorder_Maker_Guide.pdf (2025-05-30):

V2.0 | JUNE 2024

## Open Playback Recorder

## MAKER GUIDE

© 2022-2024 by Neil Squire Society This work is licensed under the CC BY SA 4.0 License: http://creativecommons.org/licenses/by-sa/4.0
Files available at https://github.com/makersmakingchange/Open-Playback-Recorder | Page 1 of 42

### Overview

This document contains the necessary information to build the Open Playback Recorder.

### Contents

## MAKER GUIDE

Files available at https://github.com/makersmakingchange/Open-Playback-Recorder | Page 2 of 42

## MAKER GUIDE

Files available at https://github.com/makersmakingchange/Open-Playback-Recorder | Page 3 of 42

## MAKER GUIDE

Files available at https://github.com/makersmakingchange/Open-Playback-Recorder | Page 4 of 42

### Maker Checklist

This list provides an overview of the steps required to build and deliver the device.

### Maker To Do List

Read through the Assembly Guide to become familiar with required components, tools, supplies, and safety gear and overall assembly steps.
Talk to User about customization options (e.g., color, any special requests, etc.)
Talk to user about what switches they would like
- Switches (https://www.makersmakingchange.com/s/category/assistive-devices/0ZGJR00000002Mn4AI) are a separate device that can be found on the MMC site and are not included in the files for this device. Custom toppers for the Interact Switch (https://www.makersmakingchange.com/s/product/interact-switch/01tJR000000698vYAA) can be found in the build filed for this device.
Order hardware components
Gather tools, supplies, and safety equipment. Assemble the device
Test device
Print “User Guide”

### Items to Give to User

Assembled, tested device
“User Guide”

### Tool List

- 3D printer
- Soldering iron and solder
- Small flathead screwdriver
- Small Phillips screwdriver
- ¼-20 Bolt

### Customization Guide

The device can be printed in the user’s desired colour.

The text on the enclosure can be printed in a separate colour from the enclosure to increase contrast

The base and lid can be printed in separate colours for a two tone effect

## MAKER GUIDE

Files available at https://github.com/makersmakingchange/Open-Playback-Recorder | Page 5 of 42

### 3D Printing Guide

### 3D Printing Summary

Metrics | Single Unit
Total Print Time (min) | 194 (3h14)
Total Number of Components | 9
Typical Total Mass (g) | 90
Typical Number of Print Setups | 2

### 3D Printing Settings

Print File Name | Qty | Total Print Time (hr:min) | Mass (g) | Infill (%) | Support(Y/N) | Layer Height/ Nozzle Diameter(mm) | Notes
Base.stl | 1 | 1:10 | 40 | 20 | N | 0.2/0.4
Battey Cover.stl | 1 | 0:16 | 5 | 20 | N | 0.2/0.4
3 LED Spacer.stl | 1 | 0:06 | 1 | 20 | N | 0.2/0.4
2 LED Spacer.stl | 1 | 0:05 | 1 | 20 | N | 0.2/0.4
Level Button.stl | 1 | 0:03 | 1 | 20 | N | 0.2/0.4
Lid.stl | 1 | 1:19 | 39 | 20 | N | 0.2/0.4
Play Button.stl | 1 | 0:03 | 1 | 20 | N | 0.2/0.4
Record Button.stl | 1 | 0:03 | 1 | 20 | N | 0.2/0.4
Volume Knob.stl | 1 | 0:09 | 1 | 20 | N | 0.2/0.4

### Post-Processing

- Use a hobby knife to remove any burrs or bumps

## MAKER GUIDE

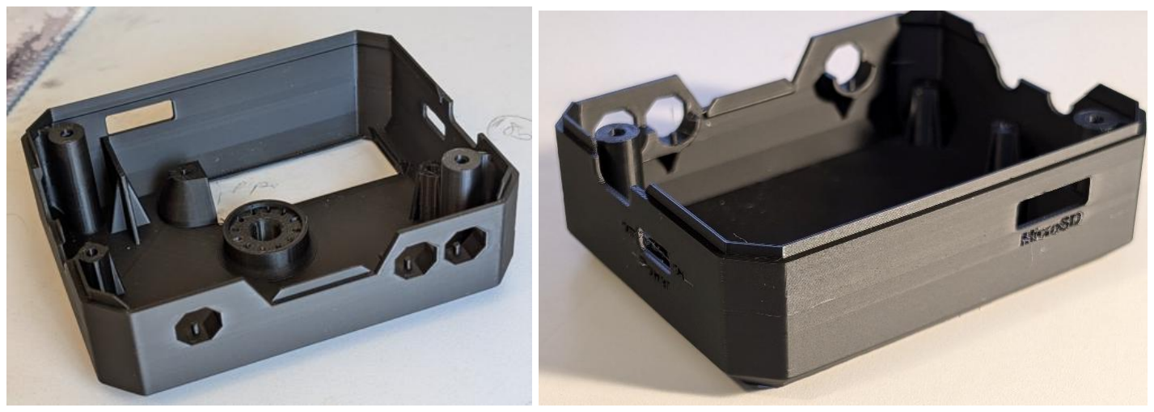
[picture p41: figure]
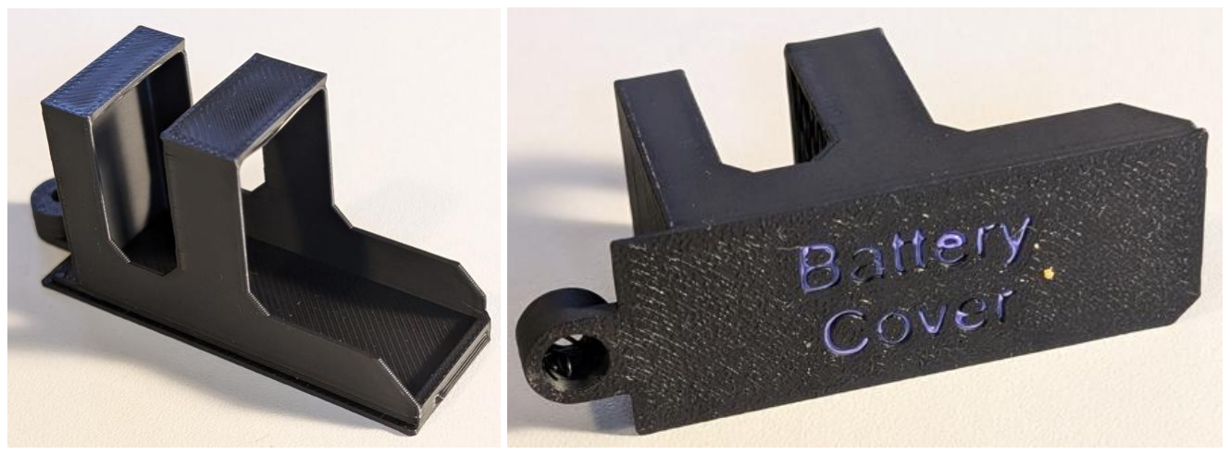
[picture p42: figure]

Files available at https://github.com/makersmakingchange/Open-Playback-Recorder | Page 6 of 42

### Examples of Quality Prints

Photo of Base.stl

Photo of Battery Cover.stl

## MAKER GUIDE

Files available at https://github.com/makersmakingchange/Open-Playback-Recorder | Page 7 of 42

Photo of Lid.stl

]Photo of Level Button.stl

## MAKER GUIDE

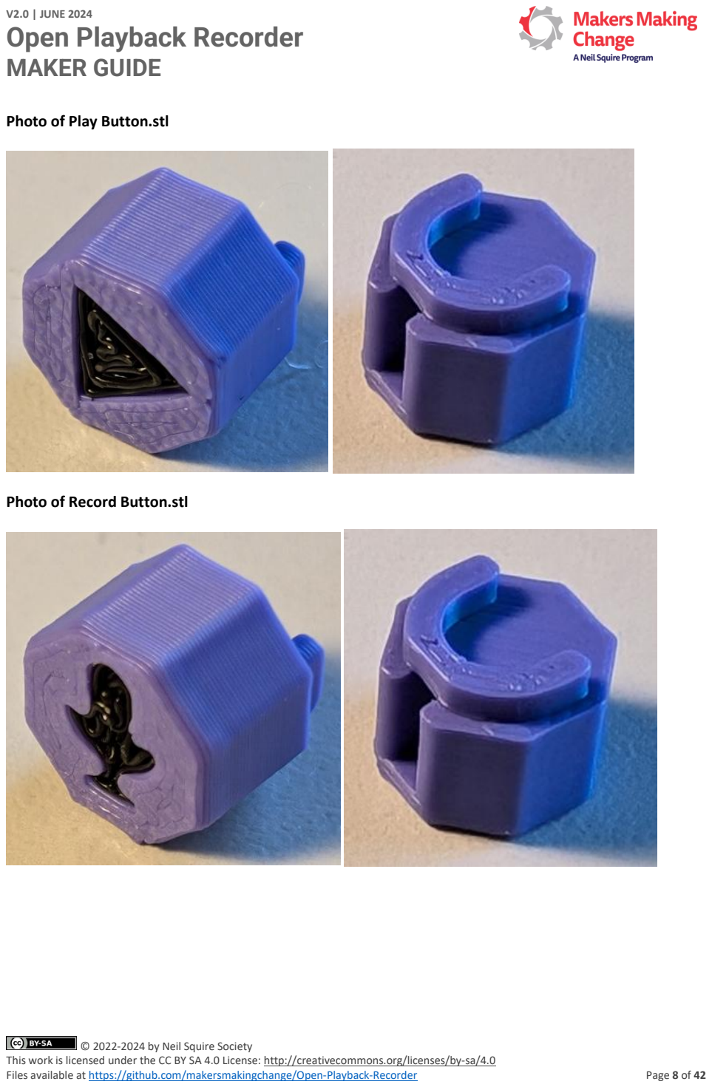
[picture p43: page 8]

Files available at https://github.com/makersmakingchange/Open-Playback-Recorder | Page 8 of 42

Photo of Play Button.stl

Photo of Record Button.stl

## MAKER GUIDE

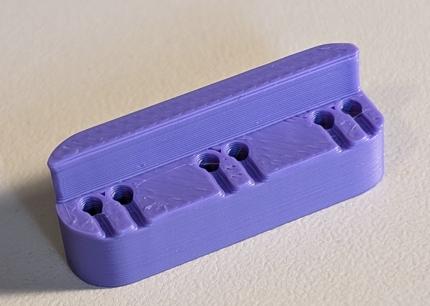
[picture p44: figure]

Files available at https://github.com/makersmakingchange/Open-Playback-Recorder | Page 9 of 42

Photo of Volume Knob.stl

Photo of 3 LED Spacer.stl

## MAKER GUIDE

Files available at https://github.com/makersmakingchange/Open-Playback-Recorder | Page 10 of 42

Photo of 2 LED Spacer.stl

### Custom Printed Circuit Board (PCB) Guide

The Open Playback Recorder uses 2 custom circuit board/boards.

The Custom PCB can be ordered from one of a variety of PCB Manufacturers. Typically, the minimum quantity for a custom PCB is five. Shipping options vary significantly in cost and shipping time. Plan on at least a week from the time of order to the PCBs arrival.

### Ordering the Custom PCB

1. Select a PCB Fabrication Company
a. JLPCB (https://jlcpcb.com/)
b. PCBWay (https://www.pcbway.com/)
c. OSH Park (https://oshpark.com/)
d. Seeed Fusion PCB (https://www.seeedstudio.com/fusion_pcb.html)
2. Create an account or use a guest login.
3. Upload both the Gerber Files (e.g., Open_Playback_Recorder_Top_2024-06-26.zip, Open_Playback_Recorder_Bottom_2024-06-26.zip).
4. Select the fabrication options for each PCB:
a. PCB Layers: 2 Layers
b. PCB Quantity: 1
c. PCB Thickness: 1.6 mm
d. Surface Finish: HASL with lead
e. PCB Color: Choose what you like. Note that certain colours may impact build time and cost.
f. The default settings for the other settings should work.
5. Select shipping option.
a. Shipping options and costs vary significantly. Select the best option based on your budget and timing.
6. Submit the order.

## MAKER GUIDE

Files available at https://github.com/makersmakingchange/Open-Playback-Recorder | Page 11 of 42

## MAKER GUIDE

Files available at https://github.com/makersmakingchange/Open-Playback-Recorder | Page 12 of 42

### Assembly Guide

### Required Components

01 | Bottom PCB | QTY:
1
02 | Battery Clip | QTY:
1
03 | 0.1 uF Capacitor | QTY:
1
04 | Slide Switch | QTY:
1

### 05 Micro SD Card

Reader

QTY:
1
06 | Press Button | QTY:
3
07 | Mono Cable Jack | QTY:
| | 2

08 15 Pin Female
Header

QTY:
2

### 09 Seeeduino

Nano

QTY:
1

## MAKER GUIDE

Files available at https://github.com/makersmakingchange/Open-Playback-Recorder | Page 13 of 42
10 | Ribbon Cable Header | QTY:

2

11 #4 Sheet Metal
Screw

QTY:
11
12 | 9V Battery | QTY:
1
13 | Level Button | QTY:
1
14 | Play Button | QTY:
1
15 | Rec Button | QTY:
1
16 | Base | QTY:
1
17 | Battery Cover | QTY:
1
18 | Micro SD Card | QTY:
1

## MAKER GUIDE

Files available at https://github.com/makersmakingchange/Open-Playback-Recorder | Page 14 of 42
19 | 2 kOhm Resistor | QTY:
5
20 | 3 LED Spacer | QTY:
1
21 | Blue LED | QTY:
3
22 | 2 LED Spacer | QTY:
1
23 | Red LED | QTY:
1
24 | Green LED | QTY:
1
25 | PAM8302 | QTY:
1

26 5 Pin Female
Header

QTY:
1
27 | MAX9814 | QTY:
1

## MAKER GUIDE

Files available at https://github.com/makersmakingchange/Open-Playback-Recorder | Page 15 of 42

28 10 kOhm Logarithmic
Potentiometer

QTY:
1
29 | Lid | QTY:
1
30 | Volume Knob | QTY:
1
31 | 4 Ohm 3W Speaker | QTY:
1
32 | Ribbon Cable | QTY:
1
33 | Top PCB | QTY:
1
34 | ¼-20 T-Nut | QTY:
| | 1

## MAKER GUIDE

Files available at https://github.com/makersmakingchange/Open-Playback-Recorder | Page 16 of 42

### Required Tools

- Soldering Iron
- Solder
- Small flathead screwdriver
- Phillips Screwdriver
- ¼-20 Bolt

### Required Personal Protective Equipment (PPE)

- Safety glasses
- Solder fume extractor (optional)

## MAKER GUIDE

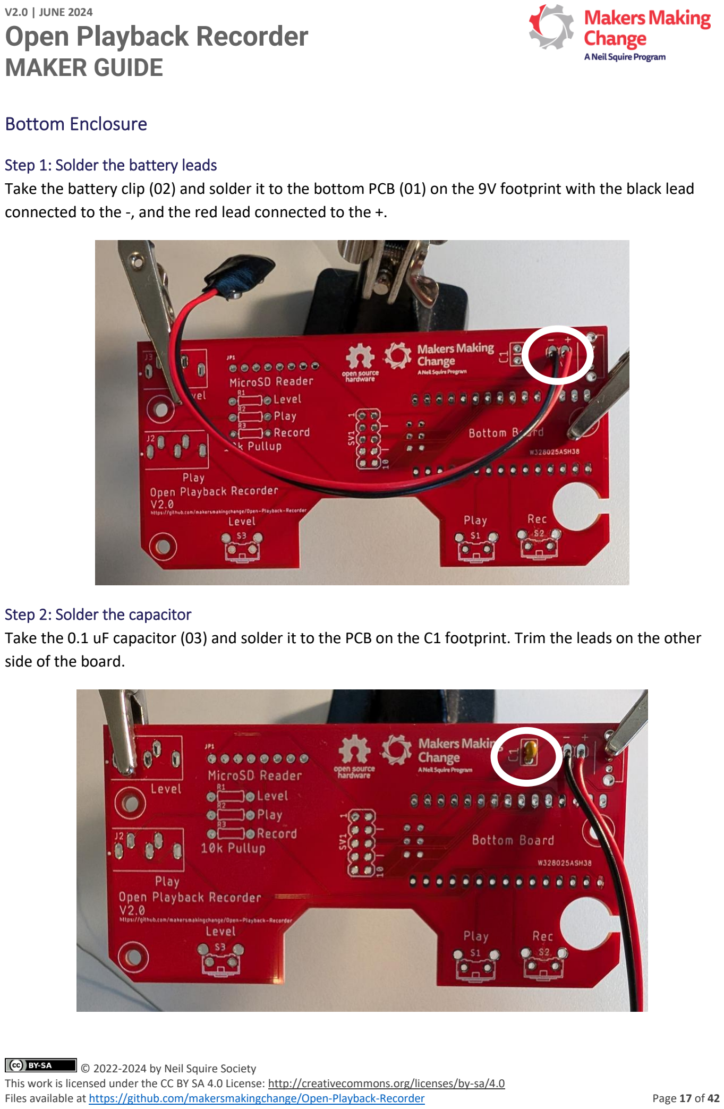
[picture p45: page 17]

Files available at https://github.com/makersmakingchange/Open-Playback-Recorder | Page 17 of 42

### Bottom Enclosure

Step 1: Solder the battery leads
Take the battery clip (02) and solder it to the bottom PCB (01) on the 9V footprint with the black lead connected to the -, and the red lead connected to the +.
Step 2: Solder the capacitor
Take the 0.1 uF capacitor (03) and solder it to the PCB on the C1 footprint. Trim the leads on the other side of the board.

## MAKER GUIDE

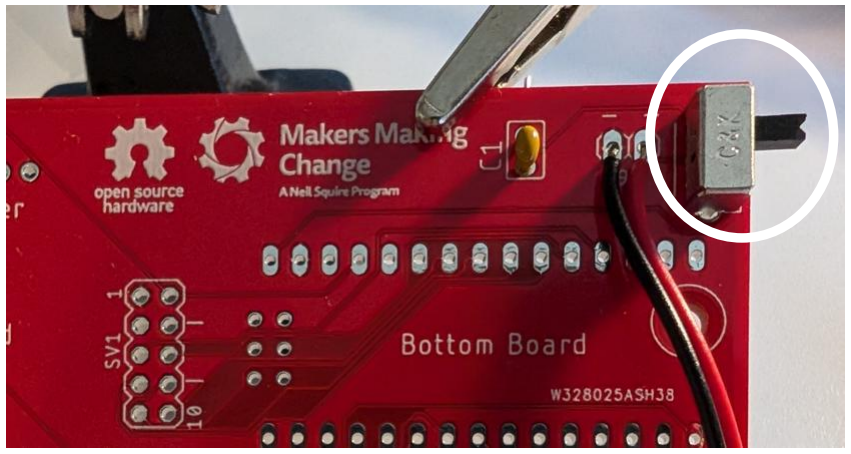
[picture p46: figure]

Files available at https://github.com/makersmakingchange/Open-Playback-Recorder | Page 18 of 42
Step 3: Solder the power switch
Take the power switch (04) and solder it to the PCB beside the battery clip, with the switch facing the side of the PCB
Step 4: Solder the headers to the MicroSD card reader
Solder the male header that came with the microSD card reader (05) to the reader with the short pins of the header in the microSD card reader and the long side of the pins facing away from the reader as shown in the below picture. Insert the microSD card (18) into the reader. You may need to trim one pin from the header that comes with the reader to get it to the correct number of pins.

## MAKER GUIDE

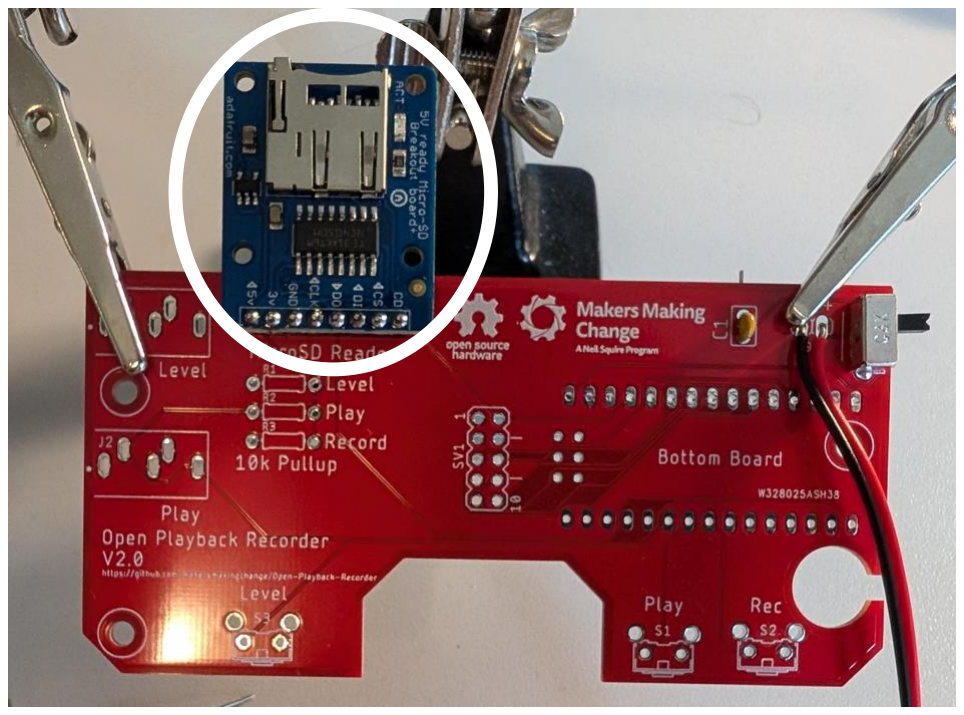
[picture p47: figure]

Files available at https://github.com/makersmakingchange/Open-Playback-Recorder | Page 19 of 42
Step 5: Solder the MicroSd card reader to the PCB
Solder the MicroSD card reader to the PCB with the SD card socket facing away from the PCB, as seen in the below photo. When soldering the reader, ensure that the board is parallel to the PCB.
Step 5: Solder the push buttons
Take the three push buttons (06) and solder them into the Level, Play, and Rec footprints on the PCB, with the button facing the edge of the board.

## MAKER GUIDE

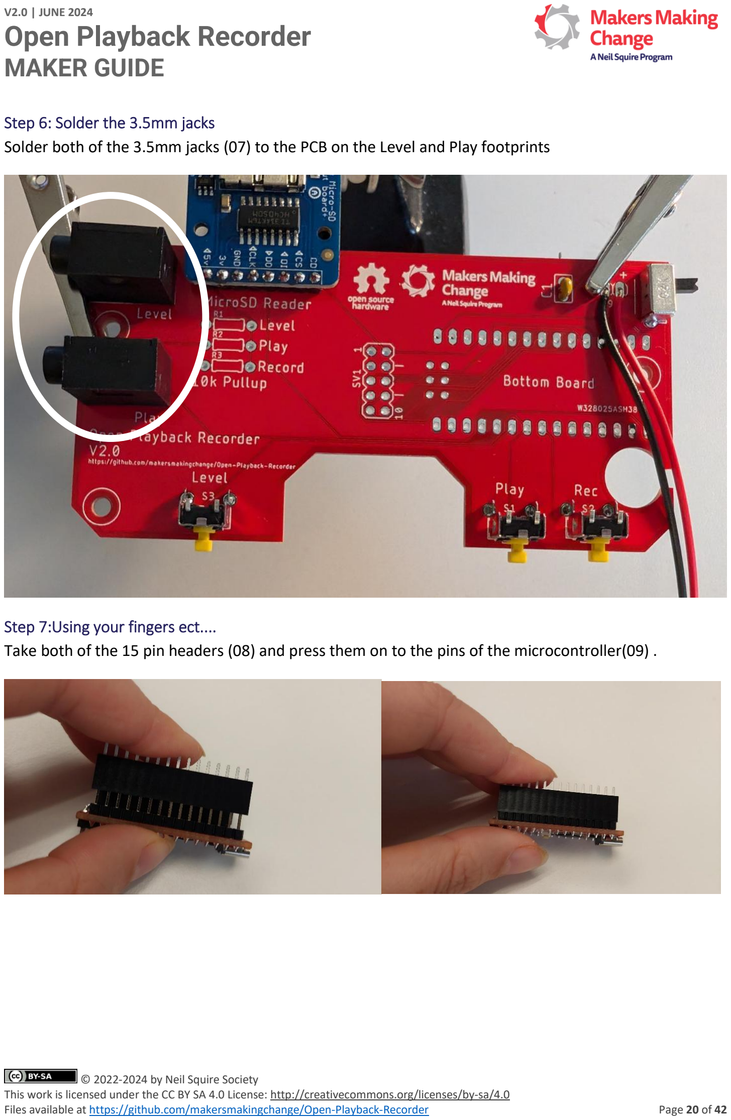
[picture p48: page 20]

Files available at https://github.com/makersmakingchange/Open-Playback-Recorder | Page 20 of 42
Step 6: Solder the 3.5mm jacks
Solder both of the 3.5mm jacks (07) to the PCB on the Level and Play footprints
Step 7:Using your fingers ect....
Take both of the 15 pin headers (08) and press them on to the pins of the microcontroller(09) .

## MAKER GUIDE

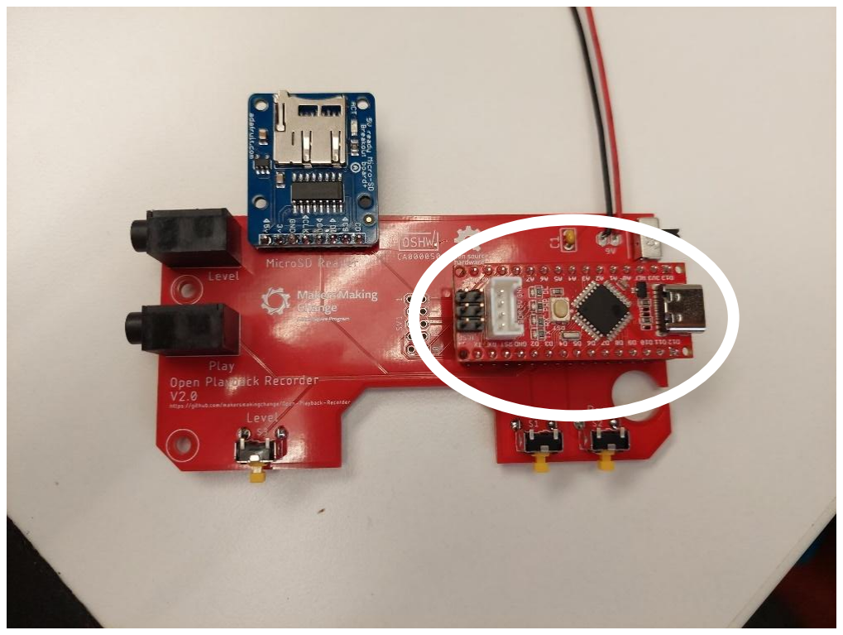
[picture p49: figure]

Files available at https://github.com/makersmakingchange/Open-Playback-Recorder | Page 21 of 42
Step 8: Solder them in place and remove the microcontroller.
Take the microcontroller with the pins attached and place it into the matching slots on the PCB. Make sure that the USB C port on the microcontroller is facing the edge of the PCB. Solder the header pins to the PCB.

## MAKER GUIDE

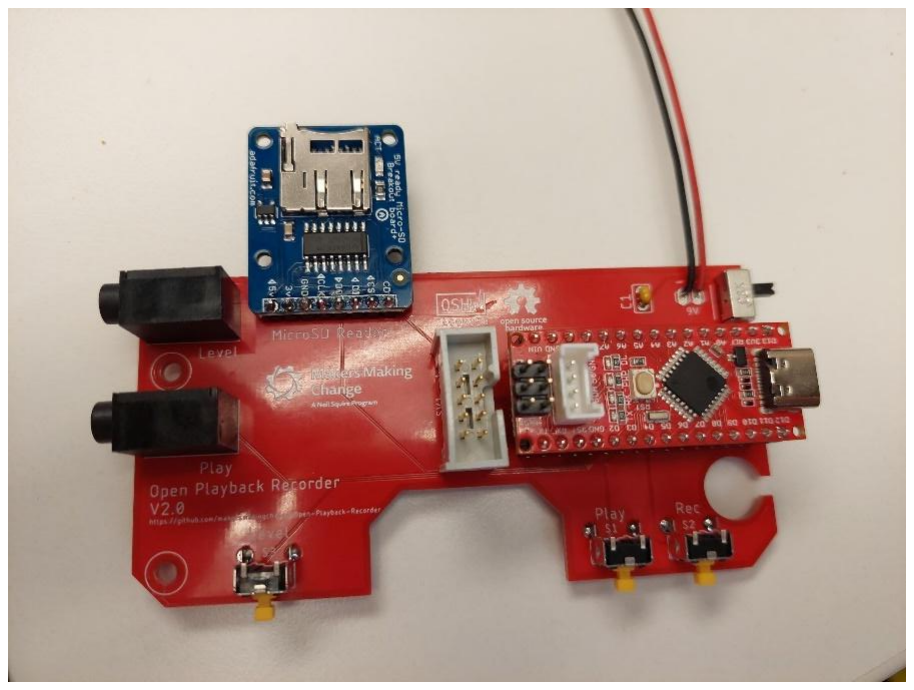
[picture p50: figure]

Files available at https://github.com/makersmakingchange/Open-Playback-Recorder | Page 22 of 42
Step 8: Solder in the ribbon cable header
Solder the ribbon cable header (10) to the SV1 footprint on the PCB. Align the gap on the header with the two lines on the footprint facing the microcontroller.

## MAKER GUIDE

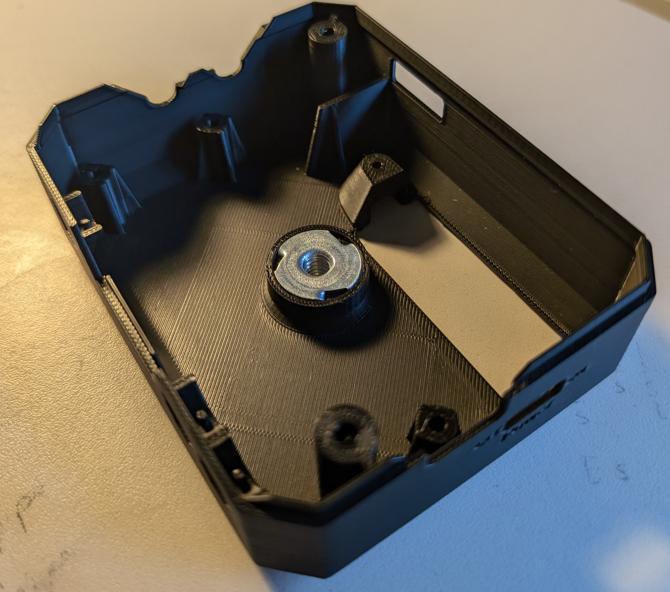
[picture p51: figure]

Files available at https://github.com/makersmakingchange/Open-Playback-Recorder | Page 23 of 42
Step 9: Add the T-Nut to the bottom enclosure
Take the T-Nut (34) and the base enclosure (16), press the T-nut into the round raised section in the middle of the base. Using a ¼-20 bolt, tighten the T-Nut in place. Remove the bolt.

## MAKER GUIDE

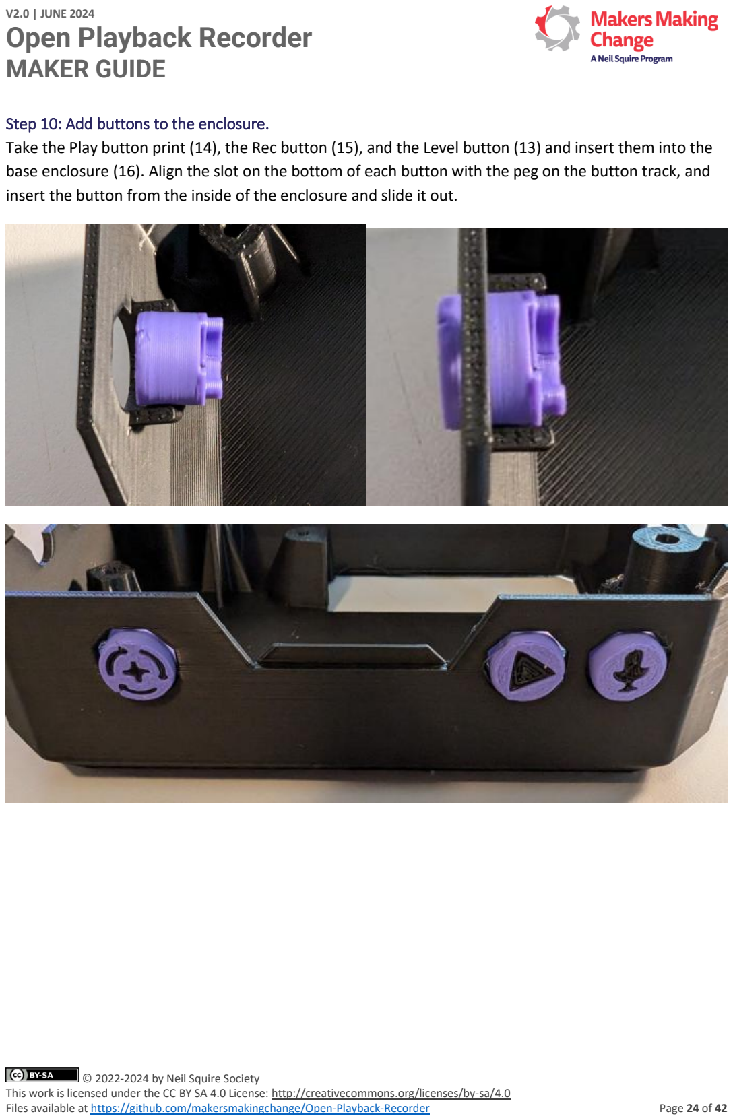
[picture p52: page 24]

Files available at https://github.com/makersmakingchange/Open-Playback-Recorder | Page 24 of 42
Step 10: Add buttons to the enclosure.
Take the Play button print (14), the Rec button (15), and the Level button (13) and insert them into the base enclosure (16). Align the slot on the bottom of each button with the peg on the button track, and insert the button from the inside of the enclosure and slide it out.

## MAKER GUIDE

Files available at https://github.com/makersmakingchange/Open-Playback-Recorder | Page 25 of 42
Step 11: Screw PCB into the bottom enclosure
Place the PCB into the enclosure so that the cutout on the board lines up with the screw boss in the enclosure and the buttons in the enclosure capture the buttons in the enclosure. Use three of the screws (11) to secure the PCB to the enclosure.

## MAKER GUIDE

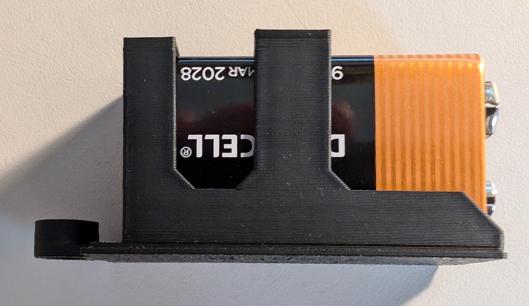
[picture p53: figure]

Files available at https://github.com/makersmakingchange/Open-Playback-Recorder | Page 26 of 42
Step 12: Connect the battery
Take the battery (12) and slide it into the battery cover (17) with the smaller terminal towards the bottom, as shown in the below photo. Pass the battery clip from the board out the battery cutout in the enclosure, and clip it to the battery. Insert the battery assembly into the enclosure and use a screw (11) to secure it in place. Slide the power switch on the enclosure to OFF.

Bottom Enclosure Done

## MAKER GUIDE

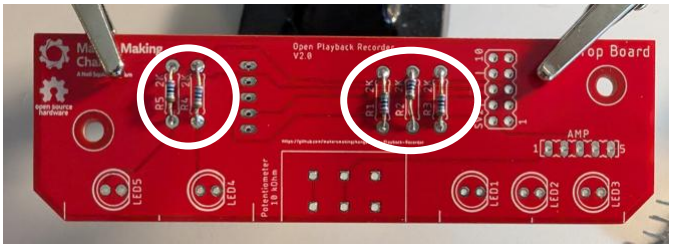
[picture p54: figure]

Files available at https://github.com/makersmakingchange/Open-Playback-Recorder | Page 27 of 42

### Top Enclosure

Step 1: Solder in the resistors
Take the resistors (19) and solder them into the R1, R2, R3, R4, and R5 footprints onto the top PCB (33). Trim the leads flush on the other side.
Step 2: Solder in the Level LEDs
Take the three blue LEDs (21) and the 3 LED spacer (20). With the flats of the LEDs facing the flat side of the spacer (circled), insert them into the spacer so that they are resting on the ledge of the spacer. When looking at the spacer from the front with the ledge in the back (Photo 1 on the left), the short leg of the LEDs should be on the right. Pass the legs of the LEDs through the footprints for LED1 LED2 and LED3 on the PCB so that the flats of the LEDs line up with the flats on the footprints. Solder the LEDs in place, then use the spacer to bend them 90 degrees so they face the side of the PCB. Trim the leads flush with the PCB.

## MAKER GUIDE

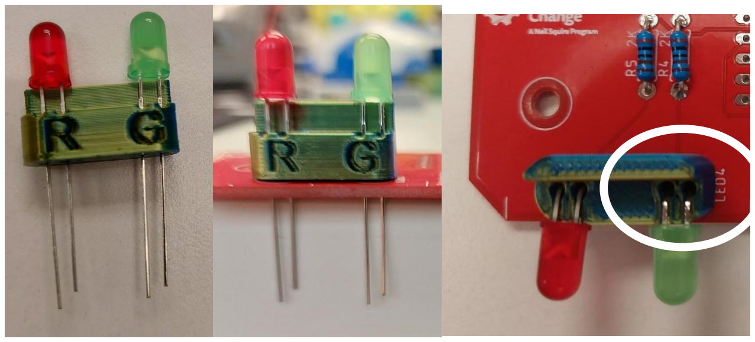
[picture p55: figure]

Files available at https://github.com/makersmakingchange/Open-Playback-Recorder | Page 28 of 42
Step 3: Solder in the Play and Rec LEDs
Take the red Rec LED (23), the green Play LED (24) and the 2 LED spacer (22). With the flats of the LEDs facing the flat side of the spacer (circled), insert them into the spacer so that they are resting on the ledge of the spacer. With the R+G label facing the front, the green LED should be inserted over the G, and the red LED should be inserted over the R. The short leg of the LEDs should be facing the right. Pass the legs of the LEDs through the footprints for LED4 and LED5 on the PCB so that the flats of the LEDs line up with the flats on the footprints. Solder the LEDs in place, then use the spacer to bend them 90 degrees so they face the side of the PCB. Trim the headers on the bottom of the PCB.
Step 4: Solder the amplifier terminal and male headers
Take the amplifier (25) and solder the male headers onto it with the short side of the headers in the board, and the long pins facing away from the board, on the side with no electronic components. You may need to trim one pin off the headers that come with the board to make them fit. Take the screw terminal blocks that came with it, and solder them to the bottom of the board with no electronic components, with the connectors facing away from the pins, as shown in the photo.

## MAKER GUIDE

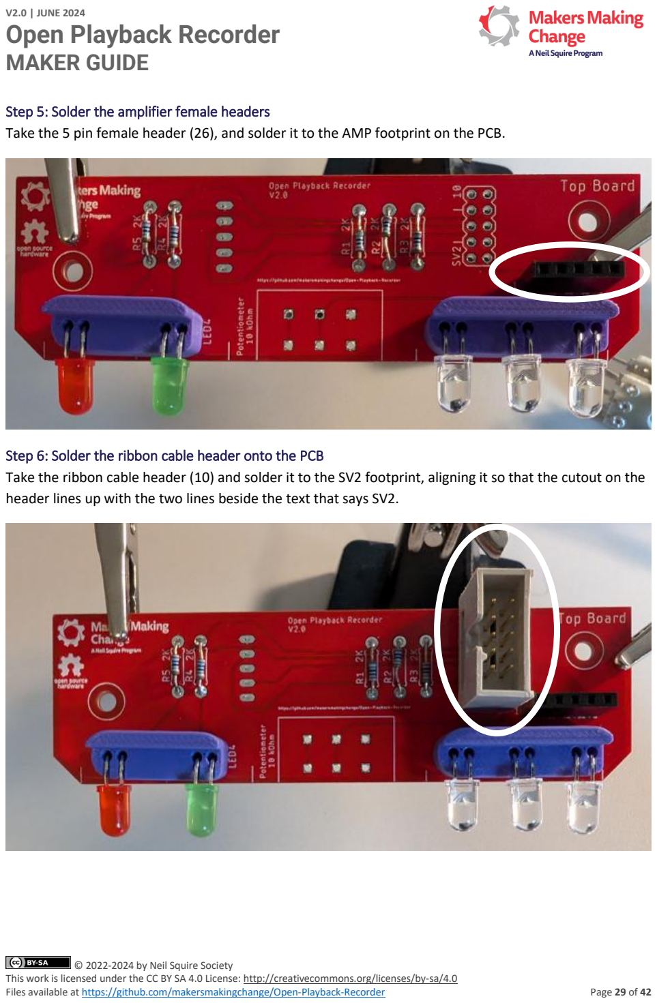
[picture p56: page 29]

Files available at https://github.com/makersmakingchange/Open-Playback-Recorder | Page 29 of 42
Step 5: Solder the amplifier female headers
Take the 5 pin female header (26), and solder it to the AMP footprint on the PCB.
Step 6: Solder the ribbon cable header onto the PCB
Take the ribbon cable header (10) and solder it to the SV2 footprint, aligning it so that the cutout on the header lines up with the two lines beside the text that says SV2.

## MAKER GUIDE

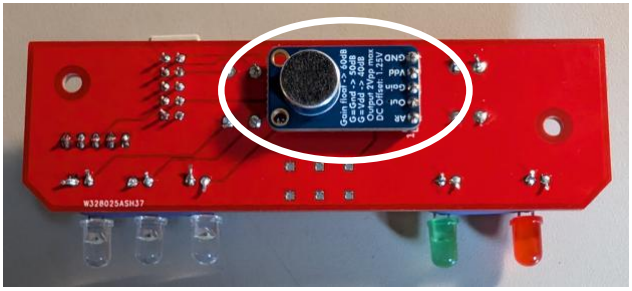
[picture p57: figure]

Files available at https://github.com/makersmakingchange/Open-Playback-Recorder | Page 30 of 42
Step 7: Solder the microphone to the PCB
Take the microphone (27) and solder it to the bottom of the PCB, aligning it so that the round microphone component on the board is roughly in the middle of the PCB. The short end of the headers should be going through the microphone and the long end through the PCB
Step 8: Solder the potentiometer into the PCB
Take the potentiometer (28) and solder it to the footprint labeled 10k Ohm so that the arm of the potentiometer is sticking out away from the board.

## MAKER GUIDE

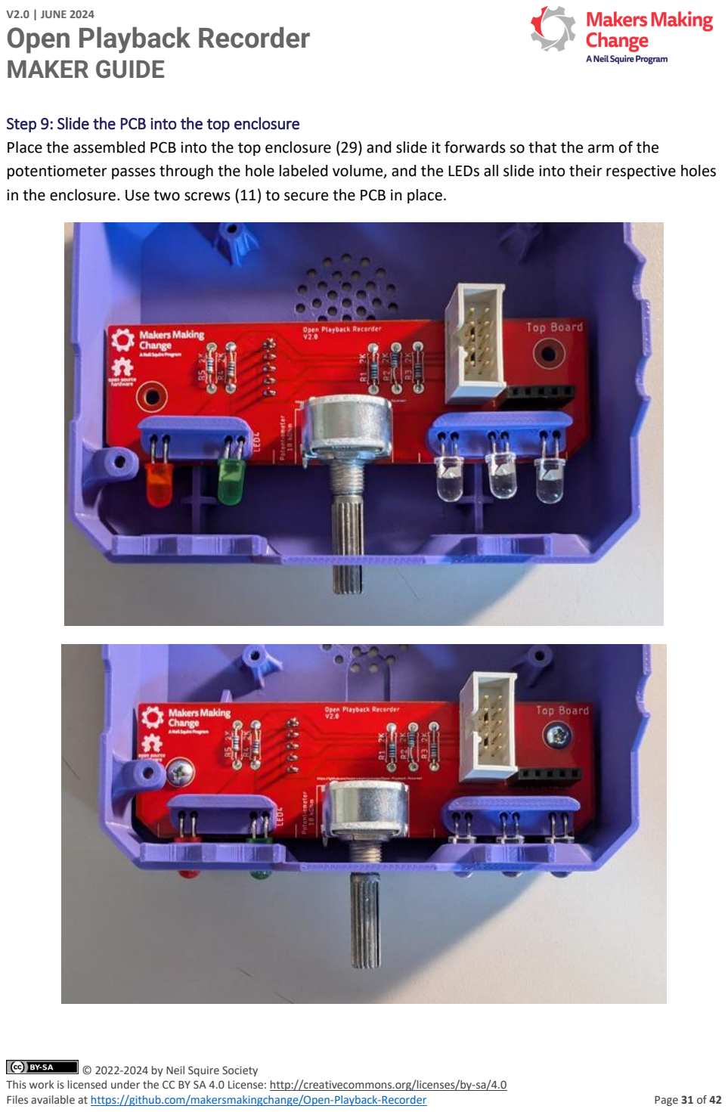
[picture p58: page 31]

Files available at https://github.com/makersmakingchange/Open-Playback-Recorder | Page 31 of 42
Step 9: Slide the PCB into the top enclosure
Place the assembled PCB into the top enclosure (29) and slide it forwards so that the arm of the potentiometer passes through the hole labeled volume, and the LEDs all slide into their respective holes in the enclosure. Use two screws (11) to secure the PCB in place.

## MAKER GUIDE

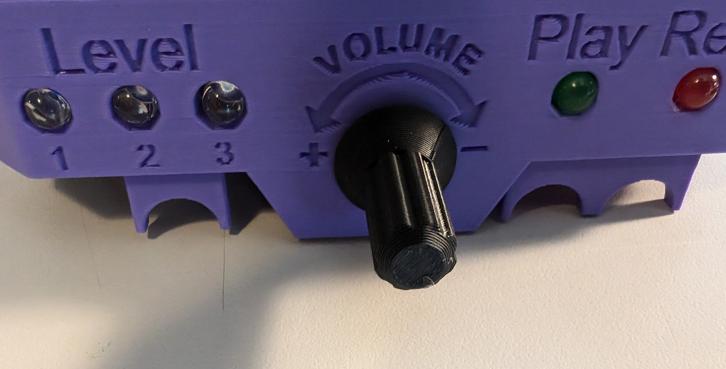
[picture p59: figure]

Files available at https://github.com/makersmakingchange/Open-Playback-Recorder | Page 32 of 42
Step 10: Attach the volume knob
Take the volume knob (30) and slide it onto the arm of the potentiometer.

## MAKER GUIDE

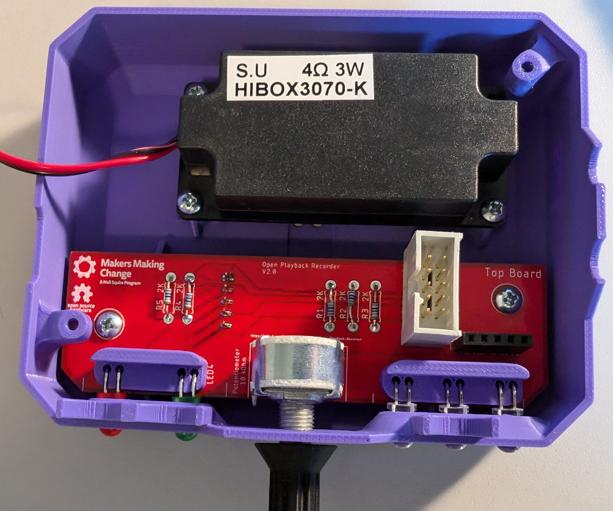
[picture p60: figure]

Files available at https://github.com/makersmakingchange/Open-Playback-Recorder | Page 33 of 42
Step 11: Prep the Speaker Wires
Take the speaker (31) and cut the lead to roughly 4 to 5 inches long. Strip 0.5cm off the ends of the wires, twist the wires together and use a bit of solder to tin them and make them solid.
Step 12: Screw the Speaker to the Enclosure
Screw the speaker onto the 4 posts in the enclosure, with the centre of the speaker over the grill in the enclosure.

## MAKER GUIDE

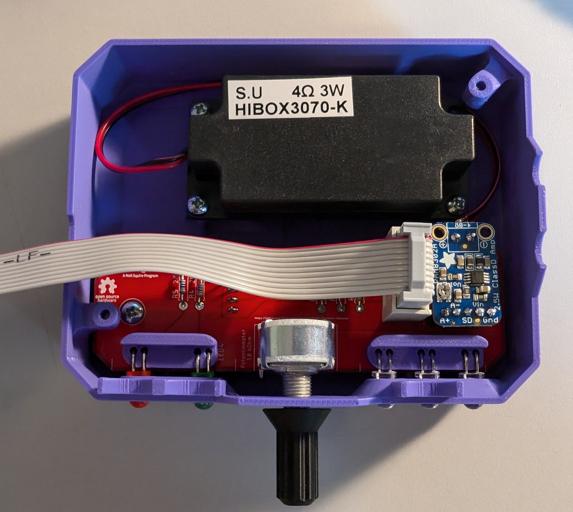
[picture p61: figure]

Files available at https://github.com/makersmakingchange/Open-Playback-Recorder | Page 34 of 42
Step 12: Connect the speaker
Take the stripped ends of the speaker wire, and screw them into the terminal blocks on the amp using the small flathead screwdriver. Plug in the amplifier to the 5 pin header on the PCB with the terminal block facing away from the LEDs.
Step 13: Connect the ribbon cable
Plug the ribbon cable (32) into the headers on both the top and bottom PCBs. The tab on the ribbon cable is on different sides on each end of the header, on the bottom PCB, the cable should be facing away from the microcontroller after being plugged into the header.

## MAKER GUIDE

Files available at https://github.com/makersmakingchange/Open-Playback-Recorder | Page 35 of 42
Step 14: Close the enclosure
Close the two halves of the enclosure and secure it with 2 screws (11).

Top Enclosure Done

## MAKER GUIDE

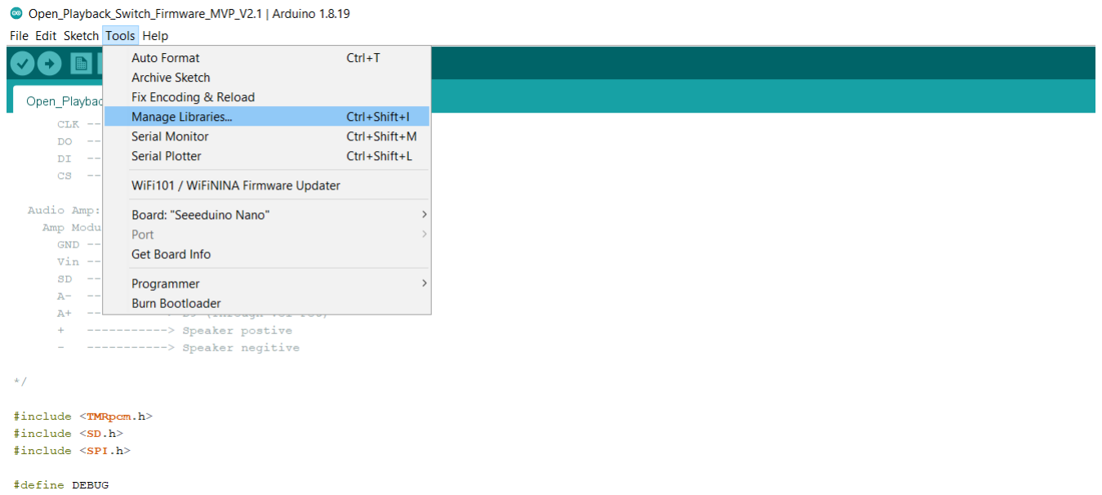
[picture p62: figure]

Files available at https://github.com/makersmakingchange/Open-Playback-Recorder | Page 36 of 42

### Programming

### Step 1: Setup Arduino IDE on Computer

1. Download Arduino IDE for your operating system at https://www.arduino.cc/en/software
2. Install the Arduino IDE.

### Step 2: Download the Firmware files

Download the firmware files from the GitHub Repository. Extract the folder to a known location and open the file in the Arduino IDE.

https://github.com/makersmakingchange/Open-Playback-Recorder/blob/main/Build_Files/Firmware_Files/Open_Playback_Recorder_Firmware.zip (https://github.com/makersmakingchange/Open-Playback-Recorder/blob/main/Build_Files/Firmware_Files/Open_Playback_Recorder_Firmware.zip)

### Step 3: Open the Library Manager

Click on the Tools menu, and select Manage Libraries. Alternatively, the menu can be opened with Ctrl+Shift+I

## MAKER GUIDE

Files available at https://github.com/makersmakingchange/Open-Playback-Recorder | Page 37 of 42

### Step 4: Search the TMRpcm library

Using the search bar on the top right of the menu, search TMRpcm. Install the library by TMRh20

### Step 5: Enable Recording

Find the folder where the TMRpcm library was installed. This is usually in C:\Users\[NAME]\sketchbook\libraries\TMRpcm. Open the file pcmConfig.h in notepad or a similar text editor.

Uncomment the line “#define buffSize 128” by removing the “//” before #define buffSize128

Uncomment the line “#define ENABLE_RECORDING” by removing the “//” before #define ENABLE_RECORDING

Save the file and close it.

## MAKER GUIDE

Files available at https://github.com/makersmakingchange/Open-Playback-Recorder | Page 38 of 42

### Step 6: Open the Preferences

Click on the File menu, and select Preferences. Alternatively, the menu can be opened with Ctrl+Comma.

## MAKER GUIDE

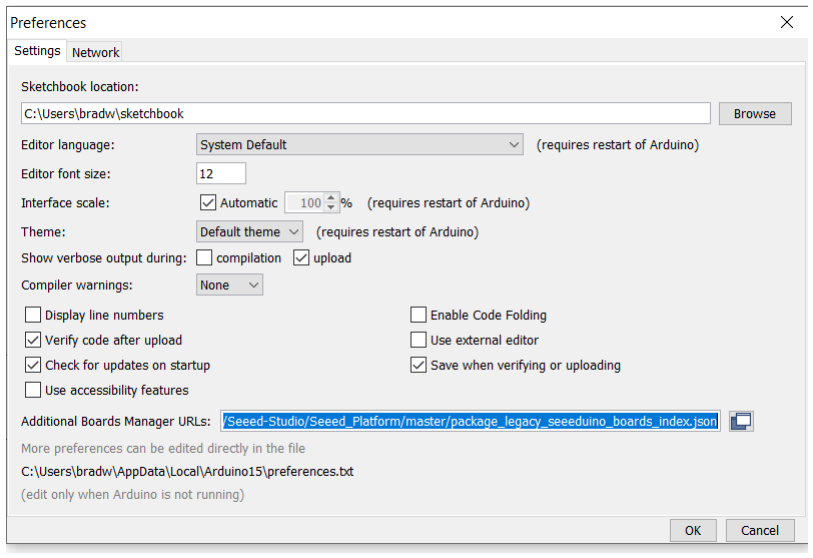
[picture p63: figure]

Files available at https://github.com/makersmakingchange/Open-Playback-Recorder | Page 39 of 42

### Step 7: Add the Board URL

Copy the following link into the Additional Board Managers URL and hit ‘OK’

https://raw.githubusercontent.com/Seeed-Studio/Seeed_Platform/master/package_legacy_seeeduino_boards_index.json (https://raw.githubusercontent.com/Seeed-Studio/Seeed_Platform/master/package_legacy_seeeduino_boards_index.json)

## MAKER GUIDE

Files available at https://github.com/makersmakingchange/Open-Playback-Recorder | Page 40 of 42

### Step 8: Add the Seeeduino Nano Board

Open the Board Manager from Tools > Board > Board Manager

Type Seeeduino AVR into the search bar, and install the board package.

## MAKER GUIDE

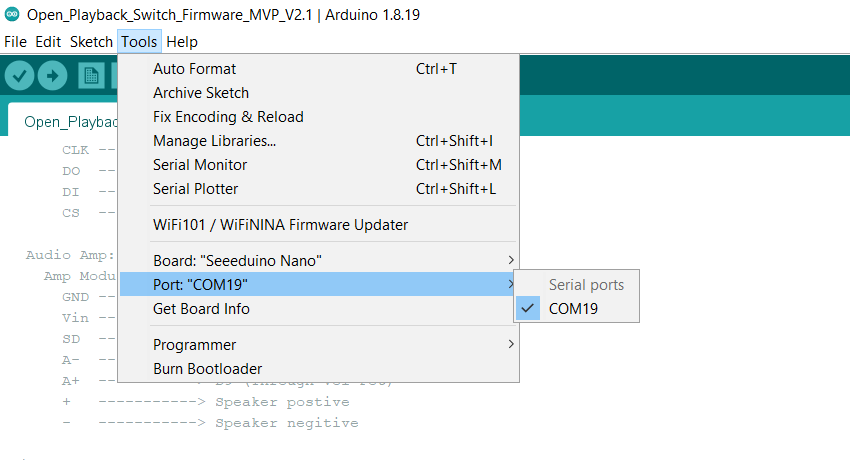
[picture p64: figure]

Files available at https://github.com/makersmakingchange/Open-Playback-Recorder | Page 41 of 42

### Step 9: Connect the Open Playback Recorder to the Computer

Plug the microcontroller into the computer using a USB cable

### Step 10: Program the Microcontroller

In the Tools menu, set the board to Seeeduino Nano, and set the port to whatever port shows up when the microcontroller is plugged into the computer. After this, press the arrow button below the Edit menu to compile the code and upload it to the microcontroller.

### Testing

Before delivering the device to the user, there are a series of tests to perform to verify that the device is working correctly.

### Power on the device with battery power

Flip the slide switch on the side of the device from off to on. The Level 1 LED should illuminate. If the Rec and Play LEDs are flashing instead, this means that there has been an issue initializing the MicroSD card.

### Record multiple messages on one level

Hold down the record button until the record LED turns on. This indicates that the device has entered record mode. At this point, holding either the play button or an assistive switch connected to the play jack will cause the device to record a message. The device will continue recording as long as the button is held down, and will finish the message when it is released. Record multiple messages, then press the record button again to exit record mode.

Pressing the play button will play the first message, and pressing it again will play the next message. Cycle through playing all the messages that were recorded until the first message is reached again.

## MAKER GUIDE

Files available at https://github.com/makersmakingchange/Open-Playback-Recorder | Page 42 of 42

### Adjust the volume

Using the volume control knob on the front of the device, change the volume while a message is playing to ensure that the volume changes as the knob is spun.

### Record a message on each level

Press either the level button, or an assistive switch connected to the level jack. The first level LED should turn off, and the second level LED should turn on. Record another message on this level, and repeat the process on the third level. Go to each level again and play back each message.

### Delete the multiple messages and record one message

Return to the first level where multiple messages were recorded and enter record mode again. Record a single message and play it back. All the previous messages should be deleted, and just the single message should play, no matter how many times the play button is pressed.

### Power the device with USB power

Flip the slide switch on the side of the device from on to off. Using a USB cable, plug the device into a computer or power block to provide power to the device. The device should power on the same as when it is on battery power, and should function the same as well.

### Troubleshooting

Both Play and Record LEDs flashing when device is powered on
This indicates that the SD card has not been properly initialized. Try reformatting the SD card, if this does not work, check the soldering on the SD card reader and the microcontroller. Finally, if neither of the previous steps work, try a new SD card.

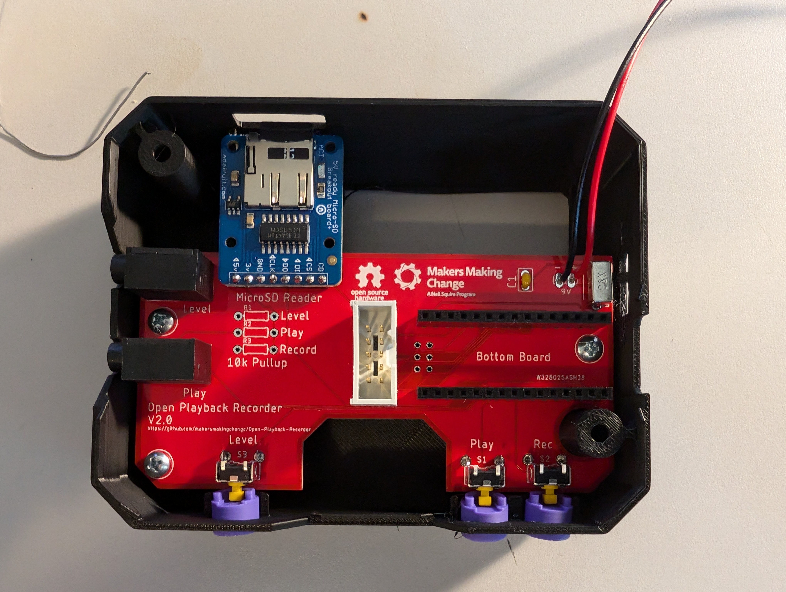
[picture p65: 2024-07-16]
Photos/Bottom PCB installed.jpg

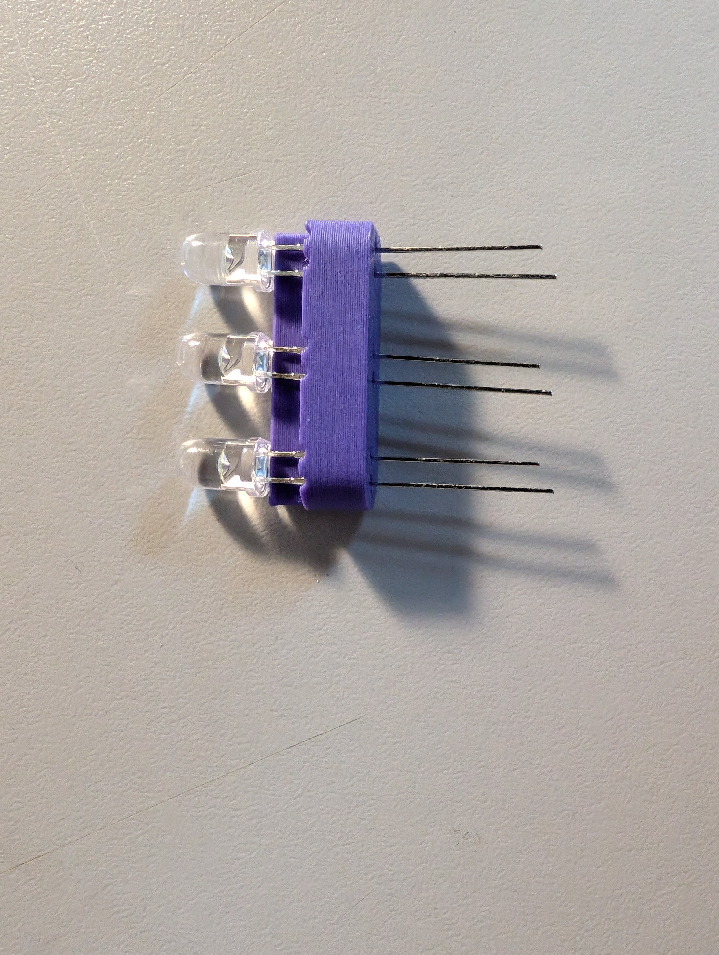
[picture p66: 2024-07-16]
Photos/Level LEDs installed in spacer.jpg

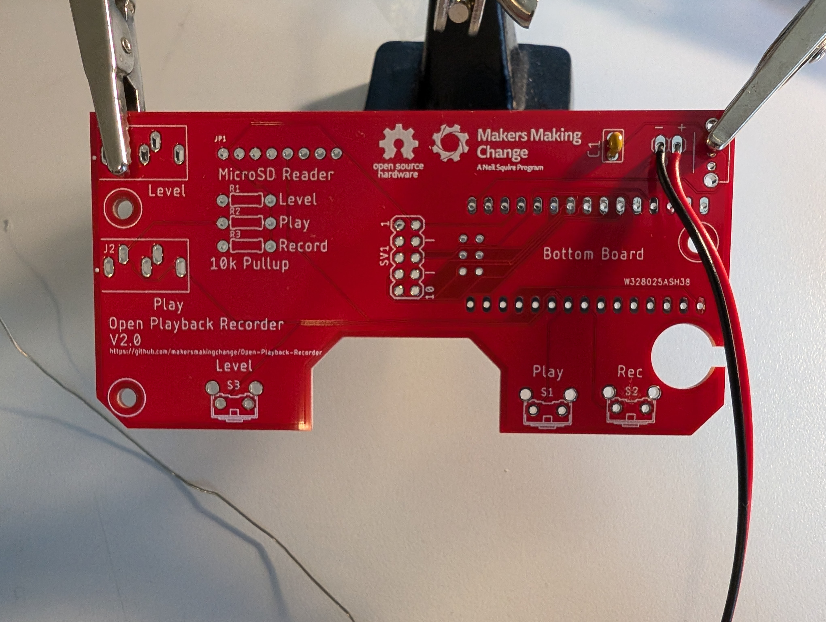
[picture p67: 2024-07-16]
Photos/Soldering capacitor to PCB.jpg

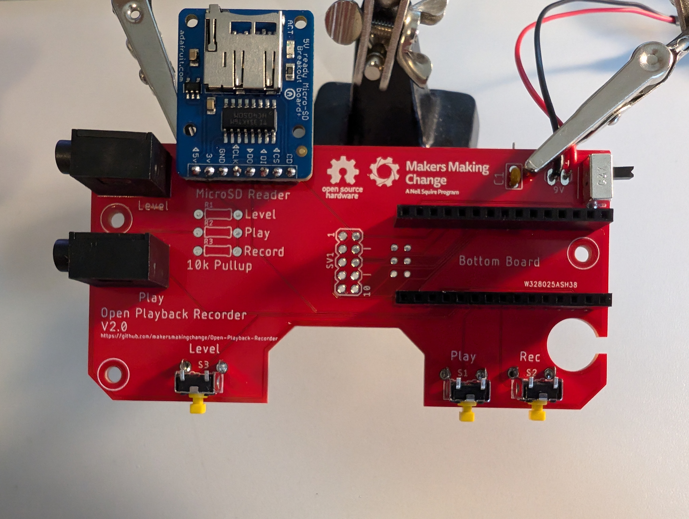
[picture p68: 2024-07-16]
Photos/Soldering microcontroller headers to PCB.jpg

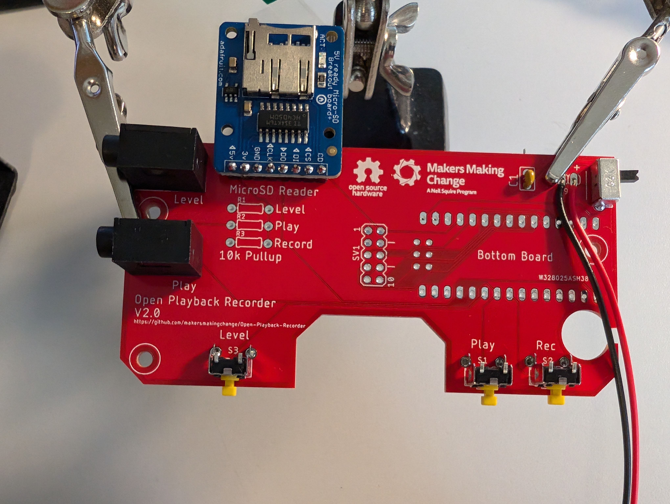
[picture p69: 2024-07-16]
Photos/Soldering jacks to PCB.jpg

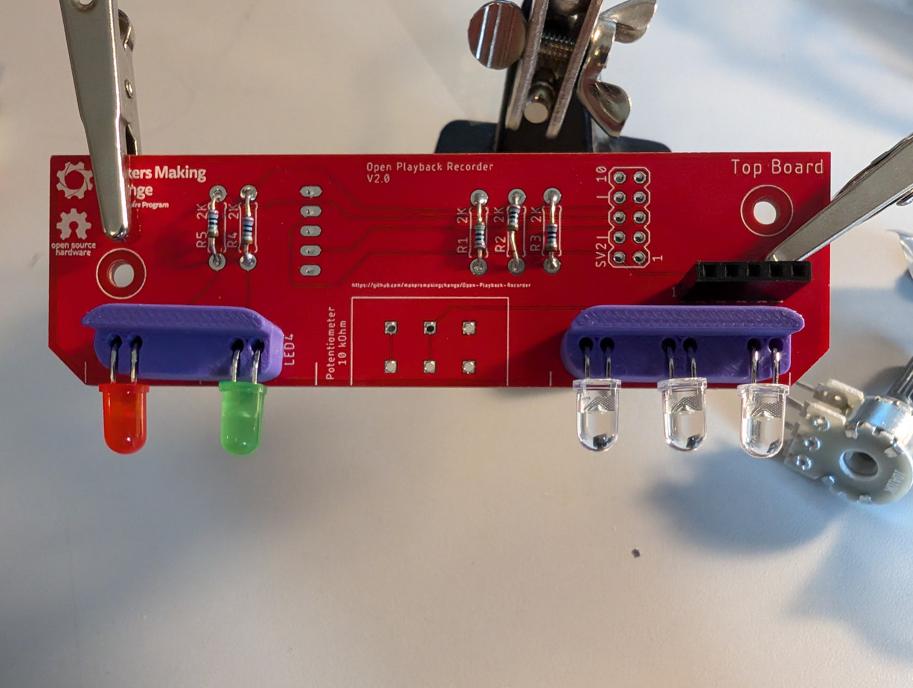
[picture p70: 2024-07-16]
Photos/Soldering 5 pin header to PCB.jpg

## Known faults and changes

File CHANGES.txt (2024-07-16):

Version 2.0 | 2024-06-26
 - Updating inital device to use a PCB
 - Redesigned the CAD to accomodate new PCB
 - Updated parts list for PCB mount components
 - Software remains the same

Version 1.0 | 2023-10-05
 - Initial Device
 - 3 Levels of stored messages
 - Play messages back one by one
 - Design and Documentation by Neil Squire Society

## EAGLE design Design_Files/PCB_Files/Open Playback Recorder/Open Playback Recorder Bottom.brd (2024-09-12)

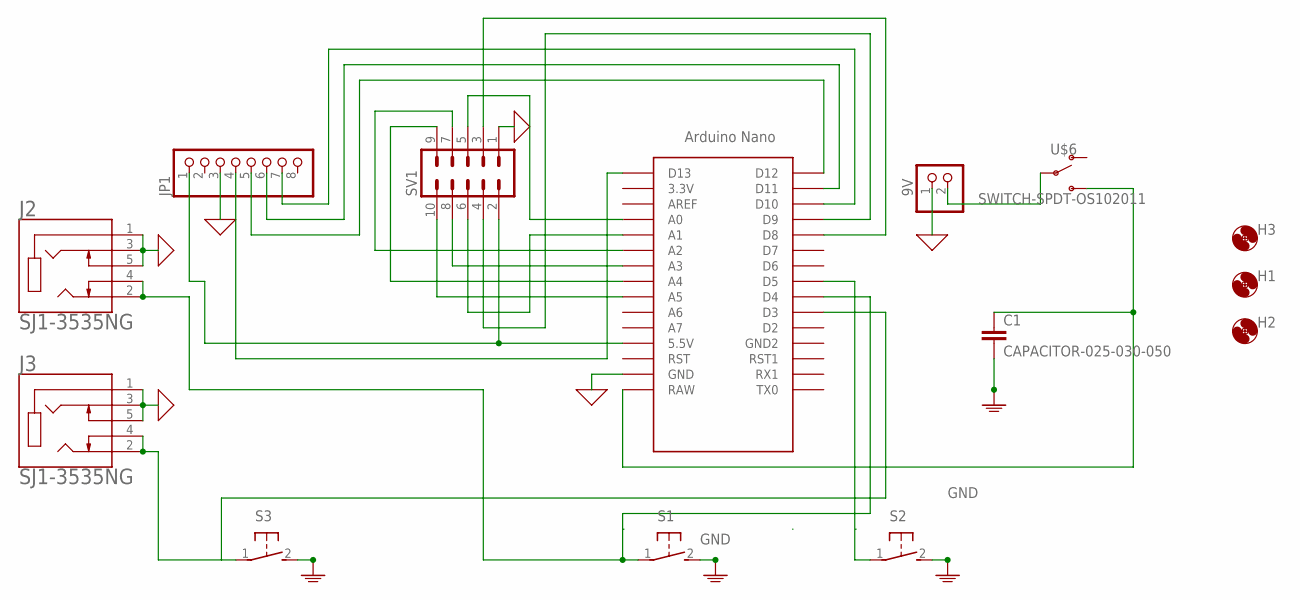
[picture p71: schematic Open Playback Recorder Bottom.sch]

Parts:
9V: PINHD-1X2; 1X02
C1: CAPACITOR-025-030-050; CAP-025-030X050
H1, H2, H3: MOUNT-HOLE-3MM-CLEAR; HOLE-3MM-CLEAR
J2, J3: SJ1-3535NG; CUI_SJ1-3535NG
JP1: HEADER_MALE-1X8ROUND; 1X08_ROUND
S1, S2, S3: SWITCH_OMRON_RA-RA; B3F-31XX
SV1: MA05-2
U$1: NANO
U$6: SWITCH-SPDT-OS102011; SWITCH_SPDT_11MA1QS1

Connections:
GND: 9V.1, J2.1, J2.3, J2.5, J3.1, J3.3, J3.5, JP1.3, S1.2, S2.2, S3.2, SV1.1, U$1.GND
GND1: C1.2
unnamed: JP1.1, SV1.2, U$1.5V (5.5V)
unnamed: 9V.2, U$6.2
unnamed: C1.1, U$1.RAW, U$6.3 (S)
unnamed: J3.2, J3.4, S3.1, U$1.D3
unnamed: J2.2, J2.4, S1.1, U$1.D4
unnamed: S2.1, U$1.D5
unnamed: SV1.10, U$1.A5
unnamed: SV1.9, U$1.A4
unnamed: SV1.8, U$1.A3
unnamed: SV1.7, U$1.A2
unnamed: SV1.6, U$1.A1
unnamed: SV1.3, U$1.D8
unnamed: SV1.4, U$1.D9
unnamed: SV1.5, U$1.A0
unnamed: JP1.7, U$1.D10
unnamed: JP1.6, U$1.D11
unnamed: JP1.5, U$1.D12
unnamed: JP1.4, U$1.D13

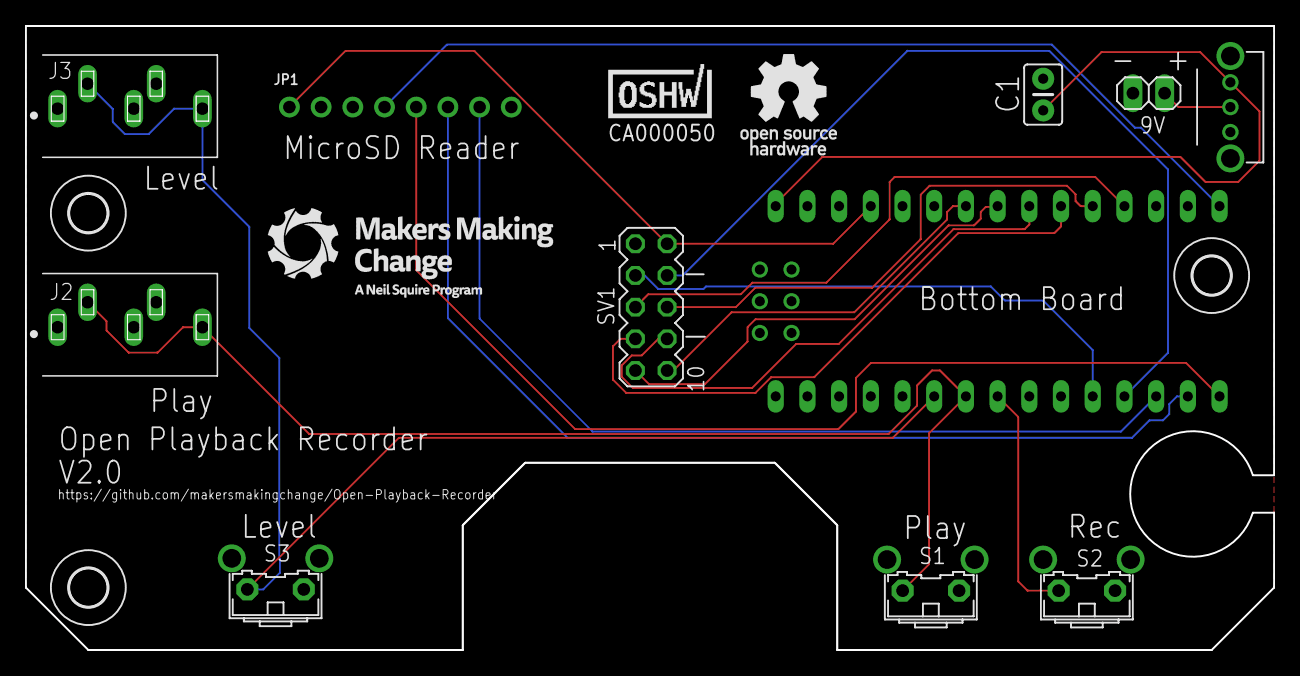
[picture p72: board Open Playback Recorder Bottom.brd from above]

Board: 2 copper layers, 100.0 x 50.0 mm, 17 parts (0 on the bottom side), 19 nets.

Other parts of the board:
U$2: CA000050; OSHWA-CERT-SMALL-SILK
U$3: MMC_MEDIUM_LOGO
U$4: OSHW_SMALL_LOGO

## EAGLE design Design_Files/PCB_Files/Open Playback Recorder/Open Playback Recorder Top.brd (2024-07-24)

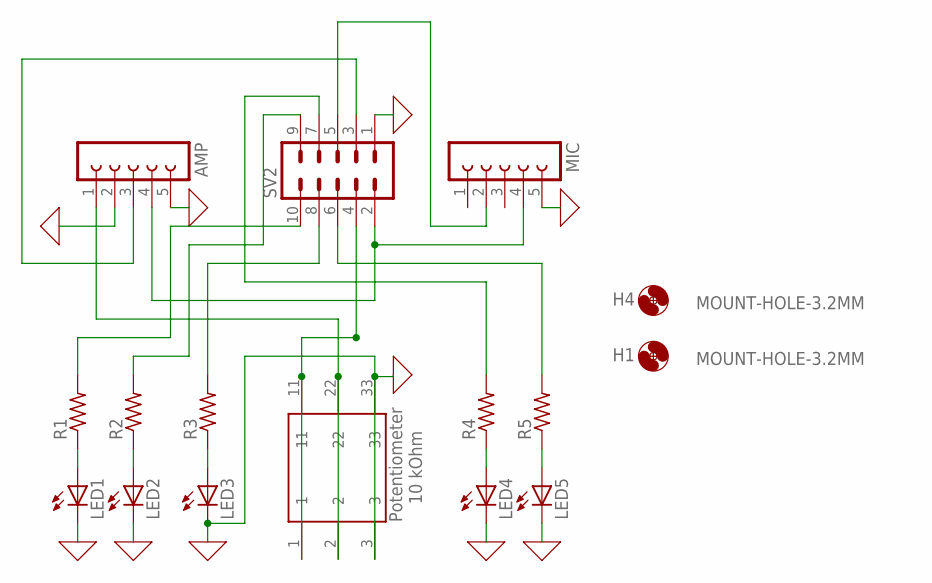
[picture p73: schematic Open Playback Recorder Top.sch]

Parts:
AMP: FE05-1
H1, H4: MOUNT-HOLE-3.2MM; HOLE-3.2MM
LED1, LED2, LED3, LED4, LED5: LED5MM
MIC: FE05-1
R1, R2, R3, R4, R5: RESISTOR-US-0206/80206/8; RESISTOR_0206/8
SV2: MA05-2
U$2: POTENTIOMETER

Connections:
GND: AMP.2, AMP.5, LED1.K (C), LED2.K (C), LED3.K (C), LED4.K (C), LED5.K (C), MIC.5, SV2.1, U$2.3, U$2.33
unnamed: LED1.A, R1.1
unnamed: LED2.A, R2.1
unnamed: LED3.A, R3.1
unnamed: LED4.A, R4.1
unnamed: LED5.A, R5.1
unnamed: SV2.4, U$2.1, U$2.11
unnamed: AMP.4, MIC.4, SV2.2
unnamed: AMP.1, U$2.2, U$2.22
unnamed: R1.2, SV2.10
unnamed: R2.2, SV2.9
unnamed: R3.2, SV2.8
unnamed: R4.2, SV2.7
unnamed: R5.2, SV2.6
unnamed: MIC.2, SV2.5
unnamed: AMP.3, SV2.3

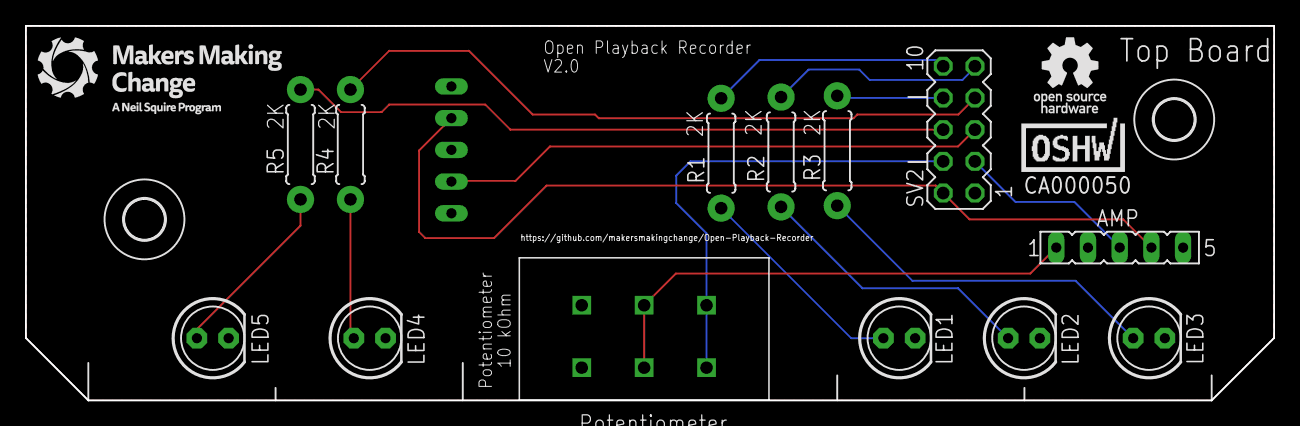
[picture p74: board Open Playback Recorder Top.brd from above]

Board: 2 copper layers, 100.0 x 30.0 mm, 19 parts (1 on the bottom side), 16 nets.

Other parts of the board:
U$1: MMC_SMALL_LOGO
U$3: OSHW_X-SMALL_LOGO
U$4: CA000050; OSHWA-CERT-SMALL-SILK

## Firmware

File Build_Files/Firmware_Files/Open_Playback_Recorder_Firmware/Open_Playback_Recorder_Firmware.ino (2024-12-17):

/* 
* File: Open_Playback_Recorder_Firmware.ino
* Developed by: MakersMakingChange
* Version: v1.0 (02 February 2024)
  License: GPL v3.0 or later

  Copyright (C) 2024 Neil Squire Society
  This program is free software: you can redistribute it and/or modify it under the terms of
  the GNU General Public License as published by the Free Software Foundation,
  either version 3 of the License, or (at your option) any later version.
  This program is distributed in the hope that it will be useful, but WITHOUT ANY WARRANTY;
  without even the implied warranty of MERCHANTABILITY or FITNESS FOR A PARTICULAR PURPOSE.
  See the GNU General Public License for more details.
  You should have received a copy of the GNU General Public License along with this program.
  If not, see <http://www.gnu.org/licenses/>

<<<<<<<< HEAD:Build_Files/Firmware_Files/Open_Playback_Switch_Firmware/Open_Playback_Recorder_Firmware.ino
  The Open Playback Button is an assistive technology device capable of recording voice messages and storing them for future playback.   
  Messages can be recorded after entering record mode by holding the record button for 2 seconds. In record mode, multiple messages can be recorded to a micro SD 
  card by pressing and holding the play button before pressing the record button again to exit record mode. The stored
  messages can then be played back with each press of the play button. An external button can be plugged into a 3.5 mm
  mono jack to act as an accessible play button.  
========

  The Open Playback Button is a device capable of recording voice messages and storing them for future playback.   
  This code will showcase the basic functionality of the device. Messages can be recorded after entering record 
  mode by holding the record button for 2 seconds. In record mode, multiple messages can be recorded to a micro SD 
  card by pressing and holding the play button before pressing the record button again to exit record mode. The stored
  messages can then be played back with each press of the play button. An external button can be plugged into a 3.5 mm
  mono jack to act as an accessible play button.  

  July 25, 2023
  Brad Wellington

  Updating code to work with the new microcontroller and include the 3 levels or recordings

  Components:

  Play button
  Record button
  Volume potentiometer with on/off switch
  play/rec leds
  3.5 mono jack

  Microphone and Amp
    MAX9814        Arduino Uno
      GND -----------> GND
      VDD -----------> 5V 
      Out -----------> A0

  Micro SD Breakout Board
    SD Module       Arduino Uno
      5V  -----------> 5V
      GND -----------> GND
      CLK -----------> SCK
      DO  -----------> MI
      DI  -----------> MO
      CS  -----------> SS

  Audio Amp: PAM8302A
    Amp Module       Arduino Uno
      GND -----------> GND
      Vin -----------> 5V
      SD  -----------> D11
      A-  -----------> GND 
      A+  -----------> D9 (Through Vol Pot)
      +   -----------> Speaker postive
      -   -----------> Speaker negitive
      
  File: Open_Playback_Recorder_Firmware.ino
  Developed by: Makers Making Change
  Version: V2.0(17 July 2024)
  License: GPL v3
  
Copyright (C) 2023-2024 Neil Squire Society
  This program is free software: you can redistribute it and/or modify it under the terms of
  the GNU General Public License as published by the Free Software Foundation,
  either version 3 of the License, or (at your option) any later version.
  This program is distributed in the hope that it will be useful, but WITHOUT ANY WARRANTY;
  without even the implied warranty of MERCHANTABILITY or FITNESS FOR A PARTICULAR PURPOSE.
  See the GNU General Public License for more details.
  You should have received a copy of the GNU General Public License along with this program.
  If not, see <http://www.gnu.org/licenses/>
  
>>>>>>>> PCB-Version:Build_Files/Firmware_Files/Open_Playback_Recorder_Firmware/Open_Playback_Recorder_Firmware.ino
*/

#include <TMRpcm.h>
#include <SD.h>
#include <SPI.h>

#define DEBUG

//-----------------------------------------------------------------------------------//
//
//***GLOBAL VARIABLE DECLARATION***//
//
//-----------------------------------------------------------------------------------//

TMRpcm audio;
File myFile;

//Additional Arduino connections
const int mic {A0};
const int rec_led {A1};
const int play_led {A2};
const int switch_jack {6};
const int rec_button {5};
const int play_button {4};
const int level_button {3};
//const int power_switch {10};
const int speaker_shutdown {8};
const int level_3 {A5};
const int level_2 {A4};
const int level_1 {A3};

//File properties
int file_number =0;
int file_level {1};
int old_level = {1};
int current_message {1};
const int sample_rate {16000};
const String file_extension {".wav"}; 
int old_file_level {1};

//-----------------------------------------------------------------------------------//
//***GET MESSAGE COUNT FUNCTION***///
//
//  This function searches the SD card and counts the total number of saved messages
//
//  Parameters  : Void
//
//  Return:     : int
//
//-----------------------------------------------------------------------------------//

int get_message_count(){
  file_number=0;
  level_check();
  int count {1};
  char file [50];
  String file_name {"rec_"};
    file_name += file_level;
    file_name += "_";
    file_name += count;
    file_name += file_extension; 
    file_name.toCharArray(file,50);
  while(SD.exists(file)){
    file_number++;
    count++;
    String file_name {"rec_"};
    file_name += file_level;
    file_name += "_";
    file_name += count;
    file_name += file_extension; 
    file_name.toCharArray(file,50);
  }
  
  #ifdef DEBUG
  Serial.print("Number of Messages: ");
  Serial.println(count);
  #endif
  
  return count;
}

void level_int(){
  file_level++;
  if(file_level>3){
    file_level=1;
  }
}

//-----------------------------------------------------------------------------------//
//***COUNT MESSAGEs FUNCTION***///
//
//  Description : This function counts the number of recordings on the current level
//
//  Parameters  : int representing the current recording level
//
//  Return:     : int representing the number of messages on the current level
//-----------------------------------------------------------------------------------//

//Function that record a message and saves it to the list of messages on the SD card.
int count_messages(int file_level){
  int numFiles = 0;
  int recNumber = 1;
  while(true){
    String file_name {"rec_"};
    file_name += file_level;
    file_name += "_";
    file_name += recNumber;
    file_name += file_extension; 
    
    //convert file name to char as defined in TMRpcm library
    char file [50];
    file_name.toCharArray(file,50);
    if(!(SD.exists(file))){
       break;
       }
    recNumber++;
    numFiles++;
  }
  Serial.print("Num Files: ");
  Serial.println(numFiles);
  return numFiles;
}

//-----------------------------------------------------------------------------------//
//***RECORD MODE CHECK FUNCTION***///
//
//  Description : This function is used to determine if the record mode should be engaged: rec button has been held for 2 seconds
//
//  Parameters  : void
//
//  Return      : bool
//
//-----------------------------------------------------------------------------------//

bool record_mode_check(){
  int timer {0};
  level_check();
  while(digitalRead(rec_button) == LOW){
    delay(100);
    timer++;

    //given rec has been held for 2 seconds, proceed to record mode and clear previous messages
    if(timer > 20){
      digitalWrite(rec_led, HIGH);
      
      #ifdef DEBUG
      Serial.println("RECORD MODE");
      #endif
      
      while(digitalRead(rec_button) == LOW){
        //wait until tell rec button is released to proceed
        
      }
      Serial.println("Getting number of files");
      file_number = count_messages(file_level);
      Serial.println("Files Counted");
      //DELETE STORED MESSAGES
      for(int i =1; i <= file_number; i++){
        String file_name {"rec_"};
        file_name += file_level;
        file_name += "_";
        file_name += i;
        file_name += file_extension; 

        //convert file name to char as defined in TMRpcm library
        char file [50];
        file_name.toCharArray(file,50);

        
        if(SD.exists(file)){
          #ifdef DEBUG
          Serial.print("Removing old message: ");
          Serial.println(file);
          #endif
          SD.remove(file_name);
          #ifdef DEBUG
          Serial.println("File removed");
          #endif
        }
      }

      //Reset file properties
      current_message = 1;
      file_number = 0;
      return true;
    }
  }
  return false;
}




//-----------------------------------------------------------------------------------//
//***PLAY MESSAGE FUNCTION***///
//
//  Description : This function will play the next message in queue
//
//  Parameters  : void
//
//  Return:     : void
//
//-----------------------------------------------------------------------------------//
 
void play_message(){
  old_file_level=file_level;
  level_check();
  if(file_level!=old_file_level){
    current_message=1;
  }
  get_message_count();
  String file_name {"rec_"};
  file_name += file_level;
  file_name += "_";
  file_name += current_message;
  file_name += file_extension; 

  //convert file name to char as defined in TMRpcm library
  char file [50];
  file_name.toCharArray(file,50);

  #ifdef DEBUG  
  Serial.print("Playing message number ");
  Serial.println(current_message);
  #endif
  
  //turn on speaker and play message
  digitalWrite(speaker_shutdown, HIGH);
  audio.play(file);

  //blink playback led until message finishes
  while(audio.isPlaying()){
    digitalWrite(play_led, LOW);
    delay(500);
    digitalWrite(play_led, HIGH);
    delay(500);
  }

  //turn speaker off
  audio.stopPlayback();
  digitalWrite(speaker_shutdown, LOW);

  //prepare next message in queue. Start at beginning if at end of queue
  current_message++;
  #ifdef DEBUG
  Serial.print("Current Message: ");
  Serial.println(current_message);
  #endif
  if(current_message > file_number){
    current_message = 1;
  }
  return;
}

//-----------------------------------------------------------------------------------//
//***LEVEL CHECK FUNCTION***///
//
//  Description : This function checks the voltage of the switch to determine the message level
//
//  Parameters  : void
//
//  Return:     : void
//-----------------------------------------------------------------------------------//

void level_check(){
  delay(75);
  if(file_level!=old_level){
  digitalWrite(level_1,LOW);
  digitalWrite(level_2,LOW);
  digitalWrite(level_3,LOW);
  #ifdef DEBUG
  Serial.print("File Level: ");
  Serial.println(file_level);
  #endif
  if(file_level==1){
    digitalWrite(level_1,HIGH);
  }
  else if(file_level==2){
    digitalWrite(level_2,HIGH);
  }
  else{
    digitalWrite(level_3,HIGH);
  }
  old_level=file_level;
  }
}



//-----------------------------------------------------------------------------------//
//***RECORD MESSAGE FUNCTION***///
//
//  Description : This function records a message and saves it to the queue of messages saved to the SD card
//
//  Parameters  : void
//
//  Return:     : void
//-----------------------------------------------------------------------------------//
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

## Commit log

2024-02-07 Fixed print files link in readme
2024-02-22 V1.0 Pre-publish review
    [Open_Playback_Recorder_BOM.csv, Open_Playback_Recorder_BOM.xlsx, Open_Playback_Recorder_BOM_V1.0.xlsx]
2024-07-16 PCB Version
    Initial push of the files for the PCB version of the Open Playback Recorder
    [2 LED Spacer.stl, 3 LED Spacer.stl, Base.stl, Battery Cover.stl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]
2024-07-16 Initial Review Changes
    -Cleaned up ReadMe
    -Renamed several unnamed photos
    -Added Step files to design files
    -Added license to firmware
    -Added images of PCB layout and schematics
2024-07-16 Fixed Merge Errors
    [Open_Playback_Recorder_BOM.xlsx]
2024-07-24 Updated files with OSHWA Certification
    [Base.stl, Lid.stl, Open Playback Recorder Bottom.brd, Open Playback Recorder Top.brd]
2024-09-12 Minor changes to build files
    [2 LED Spacer.stl, Base.stl, Lid.stl, Open Playback Recorder Bottom.brd]
2024-12-17 Updated initial value of current message
    Changed initial value of current message from 0 to 1, fixing the blank message issue on startup
2025-02-28 Added interact switch toppers
    Added custom interact toppers that match the level and play buttons on the OPR
    [Interact Topper - Level.stl, Interact Topper - Play.stl]
2025-03-26 Updating button part number
    Updated part number for button in the BoM
    [Open_Playback_Recorder_BOM.xlsx]
2025-05-30 Improved device lid
    Moved location of one of the rails on the lid to prevent it from rubbing on the PCB
    [Lid.stl]
